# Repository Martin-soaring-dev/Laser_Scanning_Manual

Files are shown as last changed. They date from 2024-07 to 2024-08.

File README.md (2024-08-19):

# Extrusion 3D printer with integrated laser profile sensor - in NUS

[TOC]

## 一、简介（Introduction）

2D激光轮廓传感器(2D Laser profile sensor)集成到3D打印机中以实现3D扫描，如下所示。

该系统由传感器、运动控制平台(motion control platform)和气动挤压系统(pneumatic extrusion system)组成，通过以太网(Ethernet)或串口(Serial Port)与PC机连接。

打印Gcode由开源切片软件生成，并由开源用户界面(UI)软件读取和发送。

打印时，命令由PC通过串口发送到控制板，在控制板(control board)上解码并执行。

在matlab中编写了一套实现扫描功能的程序。

扫描时需要运动与传感器的协调，PC通过串口控制运动平台移动一步，再通过以太网与传感器通讯获取截面，如此循环直至扫描完成。

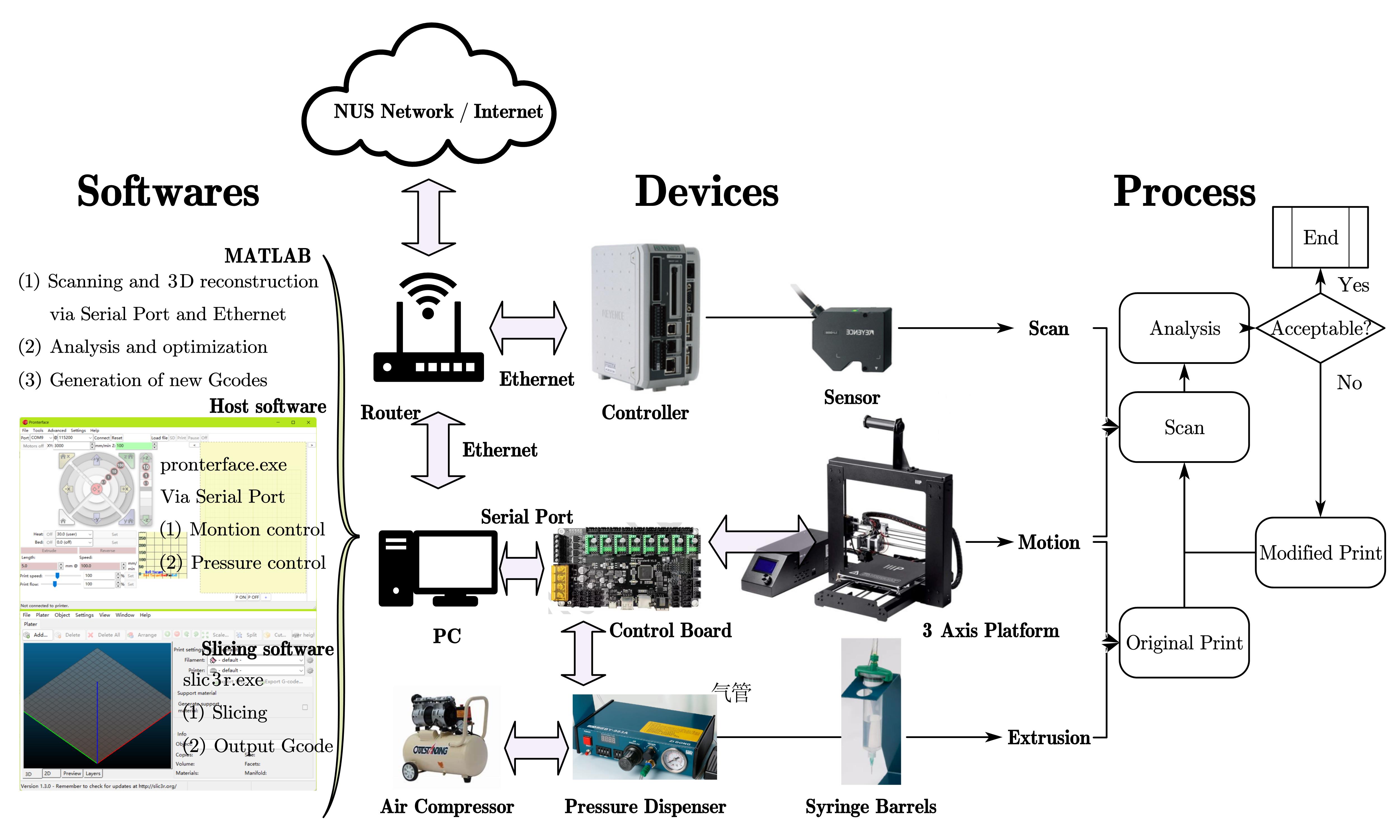
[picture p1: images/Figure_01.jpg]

图1 系统框图

### 如何从0开始搭建整个系统呢？

1. 购买/制造相应的组件，并按照设计进行装配
2. 确定各个端子的对应情况，并完成接线
3. 完成PC的环境准备、打印系统和扫描系统的配置
   1. 电脑环境的准备
   2. 打印和挤出系统的配置
   3. 扫描系统的配置

## 二、结构（Structure）

本节将介绍系统内部的主要结构。

### (1) 运动控制平台（Motion Control Platform）
运动控制平台是一个三轴钻床的基础上改装的。

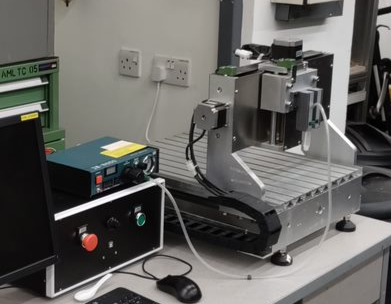
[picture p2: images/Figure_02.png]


图2 运动平台（原始） 

定制了如下组件：

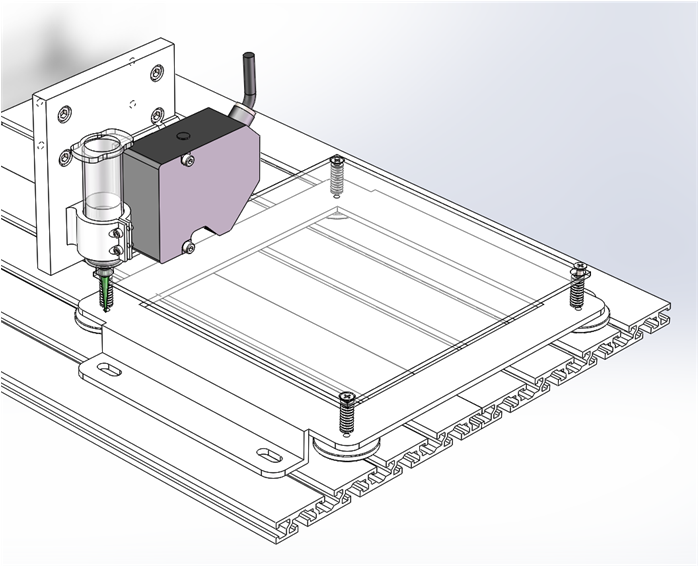
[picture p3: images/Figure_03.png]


图3 改造示意图 

#### 1）安装板
介绍：安装在Z轴滑板上的安装板，将注射器针筒和2D轮廓传感器安装在它上面。

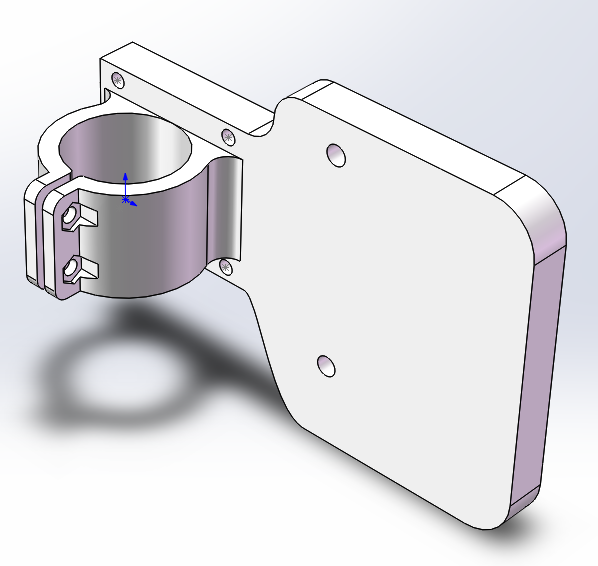
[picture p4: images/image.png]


制造：3D打印（FDM），工程塑料。

模型 3D Model：[click to get stl file](<3Dmodels/STL/安装板 - PlanB.STL>)

#### 2）底座组件

介绍：由基板、调节装置和底座构成。

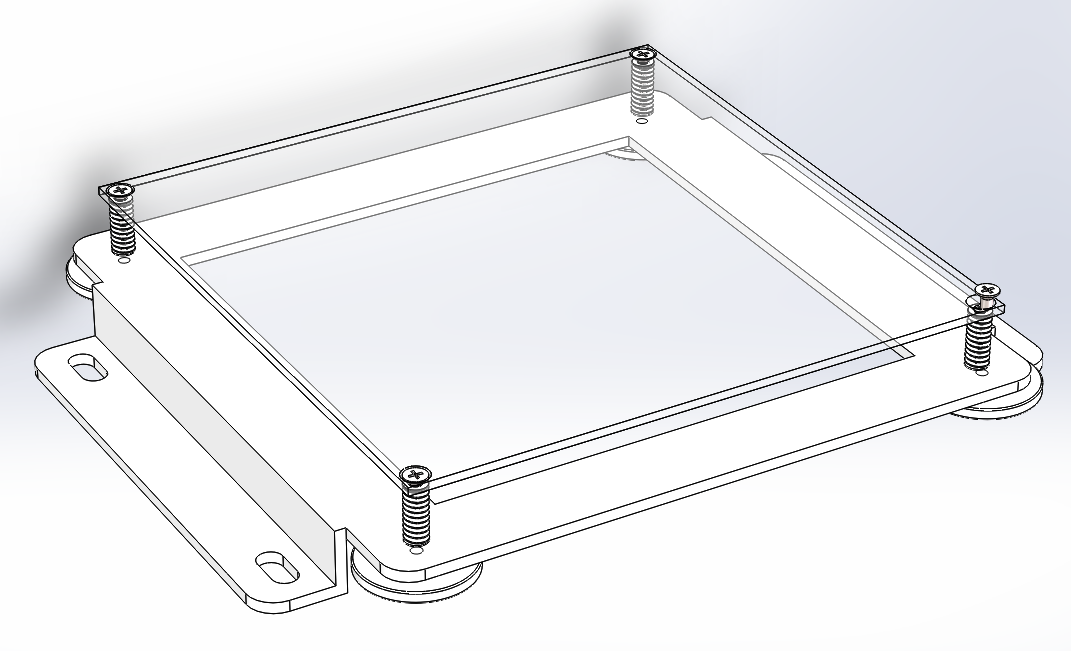
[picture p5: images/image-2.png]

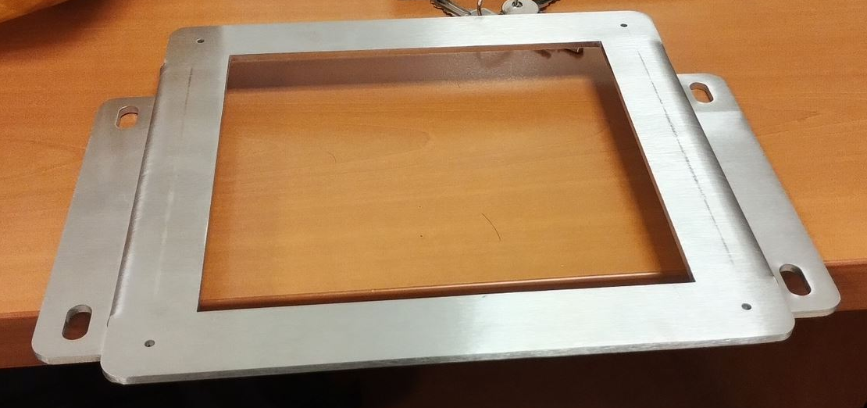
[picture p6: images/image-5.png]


制造：底座材料为不锈钢，通过激光切割和折弯制造。其余部件可直接采购。

模型 3D Model：[click to get stl file](<3Dmodels/STL/底座.STL>)

#### 3）装配体

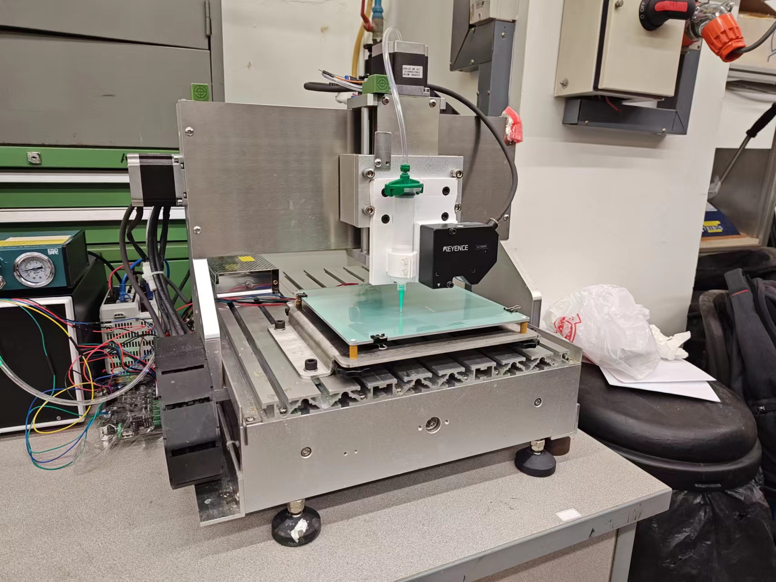
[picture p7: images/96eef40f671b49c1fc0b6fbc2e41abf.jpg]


图4 运动平台（改造后）

装配体 Assembly：[click to get stl file](<3Dmodels\STP\Assembly - Carriage-Z.STEP>)

### (2) 挤出系统（Extrusion System）
挤出系统由气压分配器和挤出装置构成。气泵可根据实验室条件选购。
#### 1）气压分配器（Pressure Dispenser）
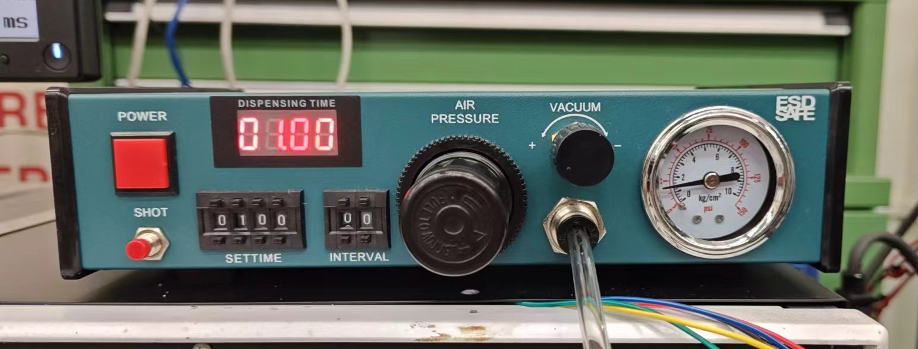
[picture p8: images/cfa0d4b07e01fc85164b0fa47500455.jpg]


图5 气压分配器

##### 技术指标：
1. 吐出方式：16种自由设定方式、带吐出时间显示*
2. 自动定时吐出：00.01S-99.99S
3. 吐出间隔时间：0.1-9.9S（自动定时功能）
4. 输入电压：220V±10% 50Hz/110V±10% 60Hz
5. 内部电压：12VDC/24VDC
6. 输入气压：10-100pSi
7. 输出气压：1-80 pSi
8.  外形尺寸：235×225×63mm
9.  重量：2.8kg
##### 使用安装说明:
位于背部的SETUP四位吐出时间编程器拨码开关，通过拨动其可作16种出方式选择模式组合设定如下：
<table>
<capital>模式组合</capital>
<tr>
<th rowspan=2 align="center">序号</th>
<th colspan=4 align="center"> 模式开关状态</th>
<th rowspan=2 align="center">吐出方式及工作对应功能</th>
</tr>
<tr>
<th align="center">S1</th>
<th align="center">S2</th>
<th align="center">S3</th>
<th align="center">S4</th>
</tr>
<tr>
<th align="center">1</th>
<th align="center">Off</th>
<th align="center">Off</th>
<th align="center">Off</th>
<th align="center">Off</th>
<th align="left">  点动模式，按下/踩下并保持以维持挤出</th>
</tr>
<tr>
<th align="center">2</th>
<th align="center">On</th>
<th align="center">Off</th>
<th align="center">On</th>
<th align="center">On</th>
<th align="left">  保持模式，按下/踩下1次开关，按照设定的时间持续挤出；再按下/踩下1次开关停止挤出。</th>
</tr>
<tr>
<th align="center">3</th>
<th align="center">Off</th>
<th align="center">On</th>
<th align="center">On</th>
<th align="center">On</th>
<th align="left">  点动计时模式，按下/踩下并保持以维持挤出设定的时间</th>
</tr>
<tr>
<th align="center">4</th>
<th align="center">On</th>
<th align="center">On</th>
<th align="center">On</th>
<th align="center">On</th>
<th align="left">  按照设定的时间自动定时连续挤出</th>
</tr>
<tr>
<th align="center">5</th>
<th align="center">On</th>
<th align="center">Off</th>
<th align="center">Off</th>
<th align="center">Off</th>
<th align="left">  按下/踩下1次开关，按设定时间挤出1次。</th>
</tr>
<tr>
<th align="center">6</th>
<th align="center">Off</th>
<th align="center">On</th>
<th align="center">Off</th>
<th align="center">Off</th>
<th align="left">  按下/踩下1次开关，按设定时间挤出2次。</th>
</tr>
<tr>
<th align="center">7</th>
<th align="center">On</th>
<th align="center">On</th>
<th align="center">Off</th>
<th align="center">Off</th>
<th align="left">  按下/踩下1次开关，按设定时间挤出3次。</th>
</tr>
<tr>
<th align="center">8</th>
<th align="center">Off</th>
<th align="center">Off</th>
<th align="center">On</th>
<th align="center">Off</th>
<th align="left">  按下/踩下1次开关，按设定时间挤出4次。</th>
</tr>
<tr>
<th align="center">9</th>
<th align="center">On</th>
<th align="center">Off</th>
<th align="center">On</th>
<th align="center">Off</th>
<th align="left">  按下/踩下1次开关，按设定时间挤出5次。</th>
</tr>
<tr>
<th align="center">10</th>
<th align="center">Off</th>
<th align="center">On</th>
<th align="center">On</th>
<th align="center">Off</th>
<th align="left">  按下/踩下1次开关，按设定时间挤出6次。</th>
</tr>
<tr>
<th align="center">11</th>
<th align="center">On</th>
<th align="center">On</th>
<th align="center">On</th>
<th align="center">Off</th>
<th align="left">  按下/踩下1次开关，按设定时间挤出7次。</th>
</tr>
<tr>
<th align="center">12</th>
<th align="center">Off</th>
<th align="center">Off</th>
<th align="center">Off</th>
<th align="center">On</th>
<th align="left">  按下/踩下1次开关，按设定时间挤出8次。</th>
</tr>
<tr>
<th align="center">13</th>
<th align="center">On</th>
<th align="center">Off</th>
<th align="center">Off</th>
<th align="center">On</th>
<th align="left">  按下/踩下1次开关，按设定时间挤出9次。</th>
</tr>
<tr>
<th align="center">14</th>
<th align="center">Off</th>
<th align="center">On</th>
<th align="center">Off</th>
<th align="center">On</th>
<th align="left">  按下/踩下1次开关，按设定时间挤出10次。</th>
</tr>
<tr>
<th align="center">15</th>
<th align="center">On</th>
<th align="center">On</th>
<th align="center">Off</th>
<th align="center">On</th>
<th align="left">  按下/踩下1次开关，按设定时间挤出11次。</th>
</tr>
<tr>
<th align="center">16</th>
<th align="center">Off</th>
<th align="center">Off</th>
<th align="center">On</th>
<th align="center">On</th>
<th align="left">  按下/踩下1次开关，按设定时间挤出12次。</th>
</tr>
</table>

实际使用的模式为序号1.

##### 操作：
1. 调压：通过调节黑色旋钮调节气压
2. 开关：可以按下左侧红色小按钮进行手动调节，也可以外接踏板手动调节（这个接口被改造用于程序控制）；控制方式在手册中有详细说明。
##### 参考资料
1. [手册](Docs/JND-983A点胶机详细功能设置.docx)

#### 2） 注射器针筒
##### 三维模型
1. [针筒](3Dmodels/SLDPRT/syringe.zip)
2. [喷嘴](3Dmodels/SLDPRT/tips.rar)
##### 手册
1. [喷嘴型号](Docs/技术表格.pdf)

### (3) 2D激光轮廓传感器（2D laser profile sensor）

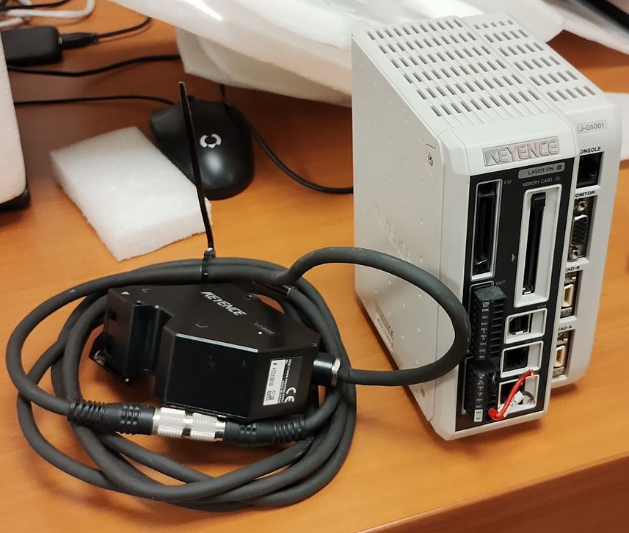
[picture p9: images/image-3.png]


图6 激光轮廓传感器

#### a. 概况：
使用的是基恩士2D激光轮廓传感器，驱动器型号为LJ-G5001，传感器型号为LJ-G030.

##### i. 驱动器：
驱动器基本安装尺寸如下所示：

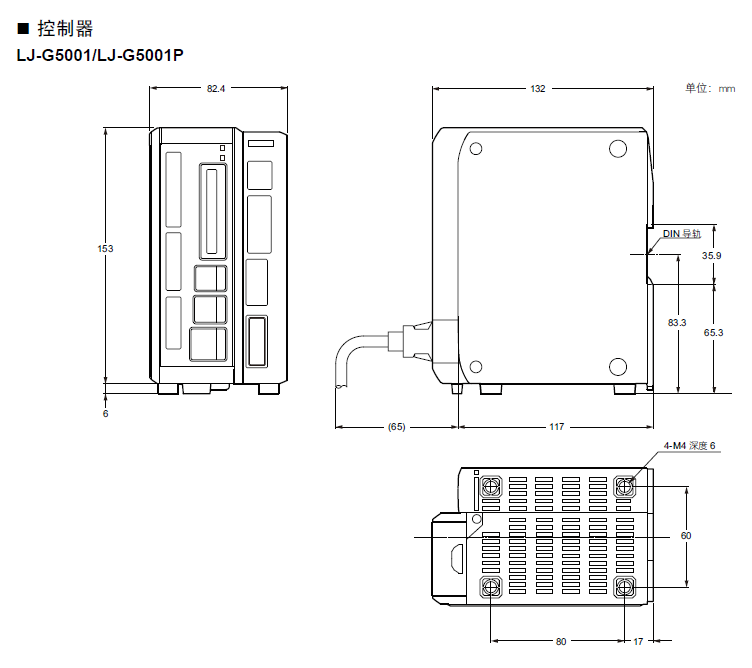
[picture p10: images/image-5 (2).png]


##### ii. 传感器：
1. 安装尺寸：

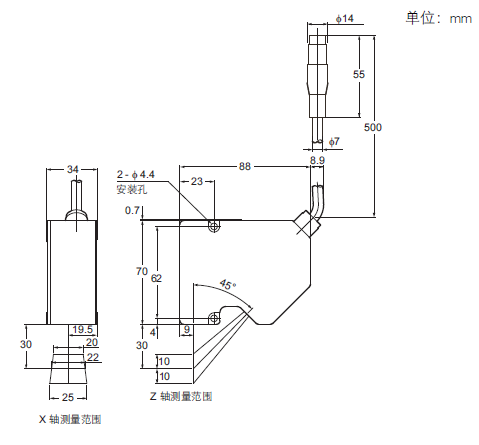
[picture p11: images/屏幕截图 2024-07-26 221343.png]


2. 测量原理及测量范围
激光轮廓传感器采用激光三角反射式原理：激光束被放大形成一条激光线投射到被测物体表面上，反射光透过高质量光学系统，被投射到成像矩阵上，经过计算得到传感器到被测表面的距离（Z 轴）和沿着激光线的位置信息（X 轴）。移动被测物体或轮廓仪探头，就可以得到一组三维测量值。

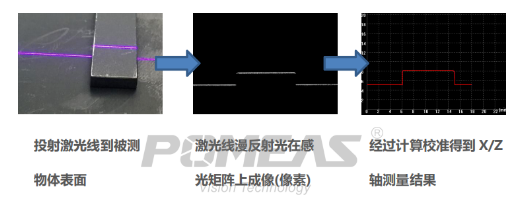
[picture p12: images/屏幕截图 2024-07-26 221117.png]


对于LJ-G030侧头，其有效测量区域为一个梯形，如下图所示：

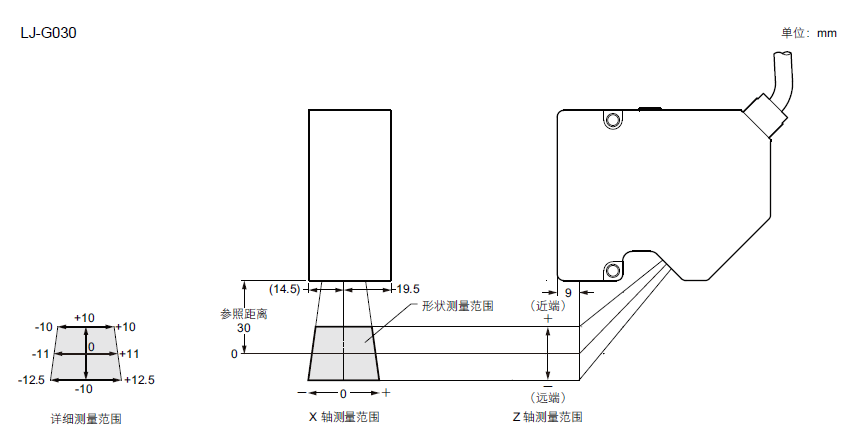
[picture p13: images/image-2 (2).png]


Z向测量范围：侧头下方30mm ± 10 mm；X向测量范围为 ±11 mm。

3. 测量精度：
Z向测量精度：1 μm. X向测量精度：5 μm。

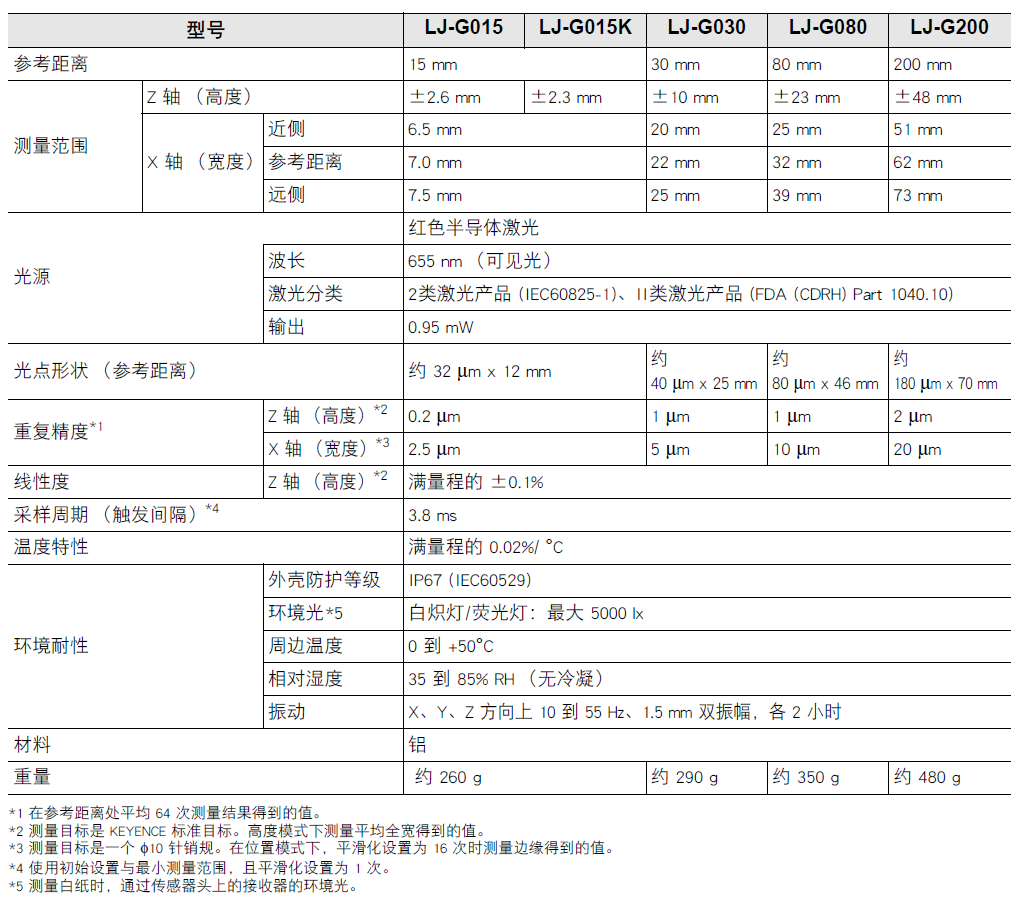
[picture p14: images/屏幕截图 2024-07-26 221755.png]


#### b. 通讯方式：

USB、串口、以太网。其中只有以太网通讯可以定制化传输轮廓数据。其他详情参见手册。
这里展示部分内容：

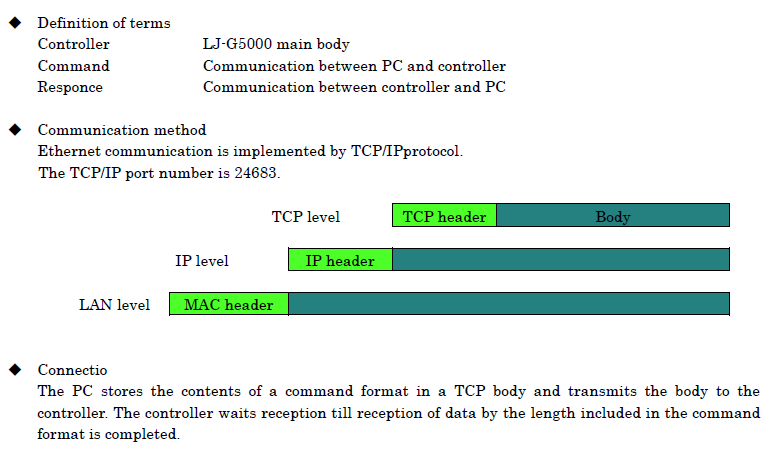
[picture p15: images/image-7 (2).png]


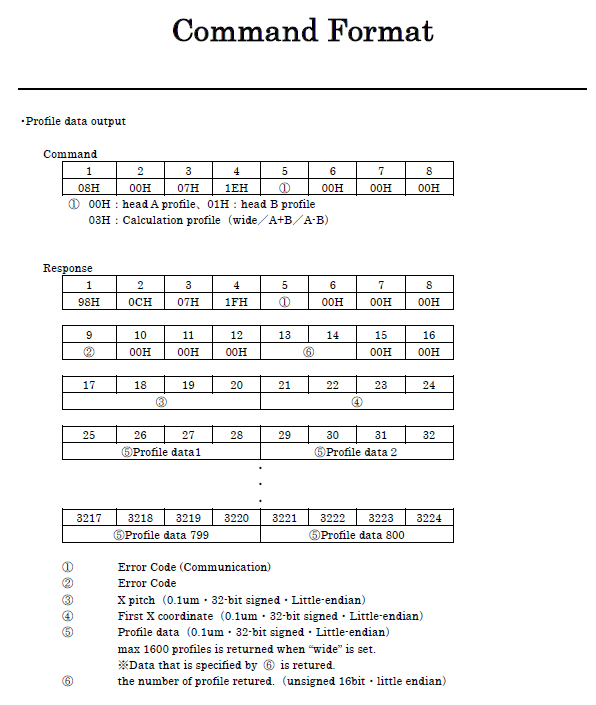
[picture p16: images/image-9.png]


#### 相关资料：
1. [用户手册](<Docs/01 AS_79826_LJ-G_UM_96M13960_CN_1059-7.pdf>)
2. [以太网通讯协议](<Docs/01 LJG5000_LAN.pdf>)
3. [LJ-G015 3D模型](Docs/LJ-G015(K)_2.x_t)
4. [LJ-G030 3D模型](Docs/LJ-G030_2.x_t)

## 三、硬件（Hardware）

这一节主要介绍接线和相关电路。

### (1) 控制板 Control borard
控制板采用了[创客基地(MakerBase)](https://makerbase.com.cn/)的[MKS-Monster8](https://github.com/makerbase-mks/MKS-Monster8)控制板。该控制板支持Marlin、Klipper等主流3D打印固件。

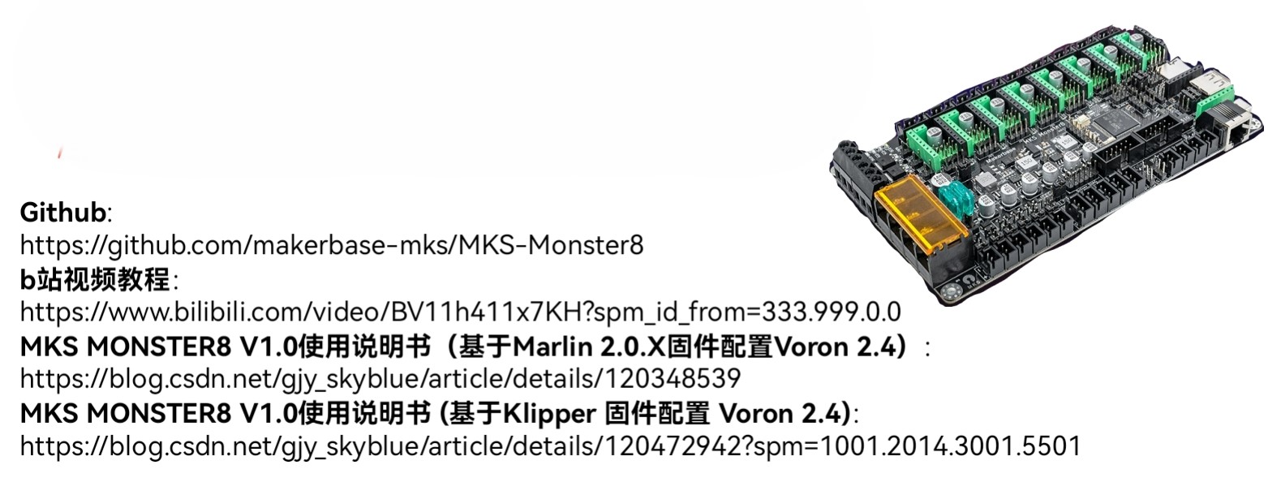
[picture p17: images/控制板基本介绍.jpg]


基本技术参数如下：
- MCU: STM32F407VET6, 168MHz, 512K flash, 192KB RAM
- 供电：DC12-24V input(2 MP1584EN Output DC12V(For FANs) and DC5V)
- 3 PWM FANs + 3 power output(all power can be select by jumper and select VIN, dc12V, dc5V)
- axis drivers and 9 motor interface(Driver0,1,2-1,2-2,3,4,5,6,7)
- EXP1,EXP2 support MKS MINI12864,MKS TS35,LCD12864,LCD2004
- USART(usart1:PA9,PA10) support MKS H43 or for other serial communication
- 6 endstop support power select(X-,X+,Y-,Y+,Z-,Z+) and 3D TOUCH(PA8) interface
- 4K eeprom on board(connect to I2C)
- Built-in CAN transceiver and interface(connect to CAN)
- Integrated SPI communication microsd card and reserved SPI signal interface
- Integrated UDISK
- Integrated virtural USB device
- Support TMC UART and SPI mode, SENSORLESS_HOMING function(Diag0-5,connect to X-,Y-,Z-,X+,Y+,Z+)
- Support driver power select(5V or 3.3V)
- Has TVS power spike protection
- Possess power reverse connection protection function
- Support DFU mode set by button(Boot0)

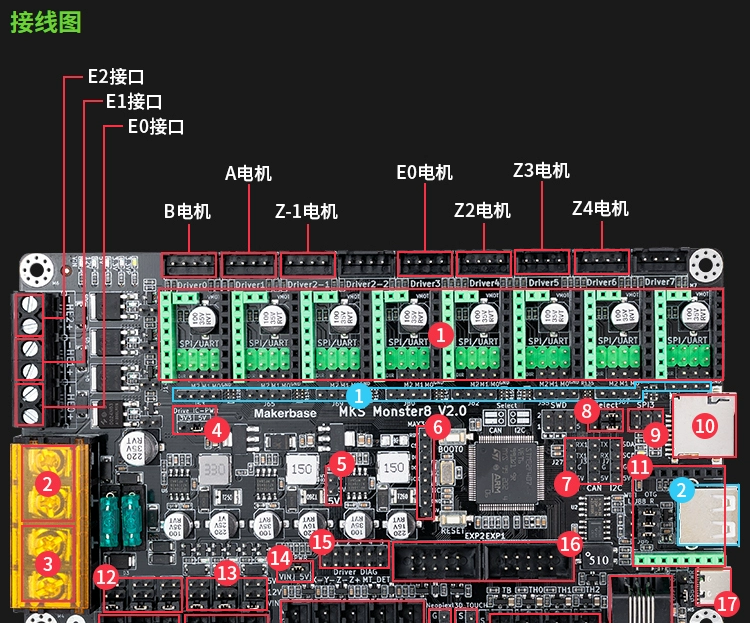
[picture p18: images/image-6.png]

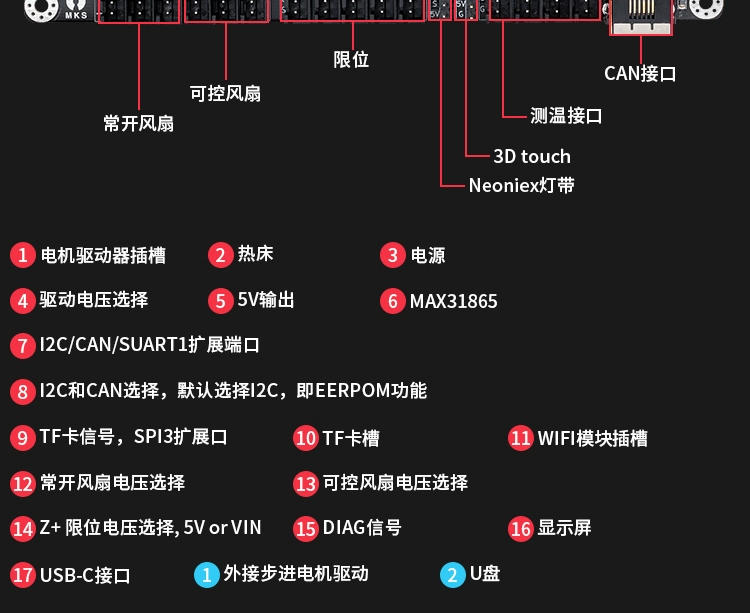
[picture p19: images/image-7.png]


但是，我们的平台需要使用的为X、Y、Z三轴的控制、无挤出加热需求、预留基板(substrate)的加热板(hot bed)，将风扇控制口留作气压开关(switch)控制，限位开关。综合上述考虑，大体的接线方案如下：

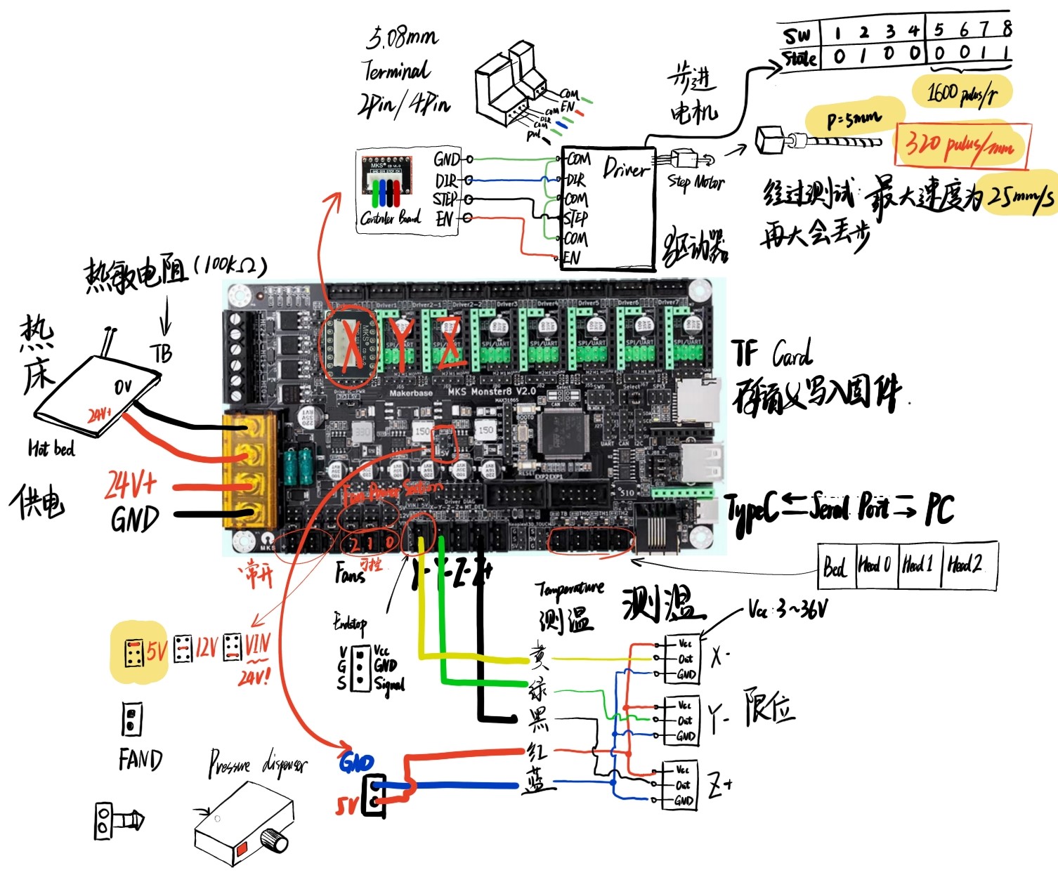
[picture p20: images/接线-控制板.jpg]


接线图

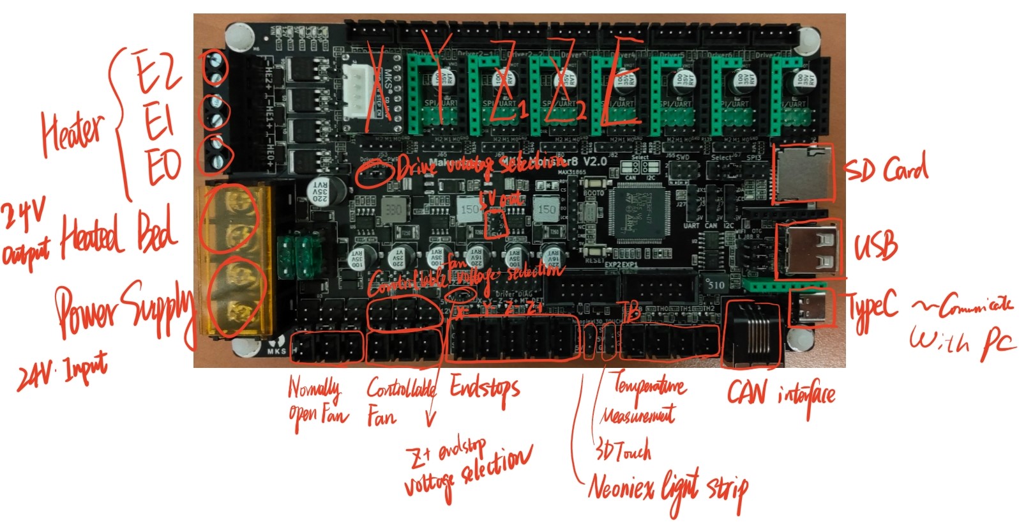
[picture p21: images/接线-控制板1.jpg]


接线图-补充

接下来我将结合这个整体接线图来说明各个部分是如何连接到控制板上的。

### (2) 电源 
电源用的就是很常见的220V交流输入，24V直流输出的电源。

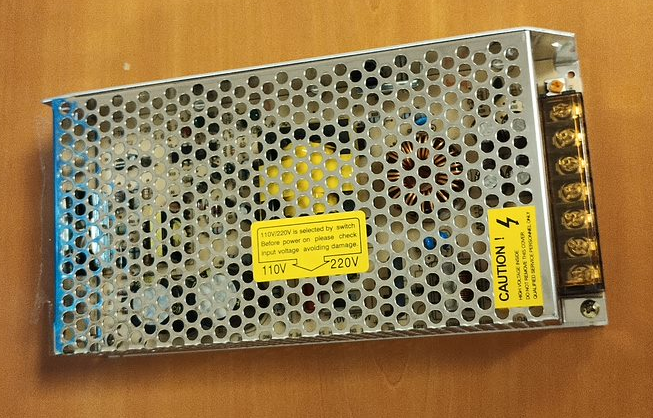
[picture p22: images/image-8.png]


图9 直流电源 Figure 9 DC power supply

### (3) 步进电机 Step Motors

所使用的点击为57步进电机。

步进电机首先与驱动器相连，驱动器需要接电源，并与控制板相连。

其控制方式为位置控制模式，即每发送一个脉冲，步进电机根据驱动器的设定转动特定的角度。对于57步进电机来说，步距角θ为0.8°（即1个脉冲对应电机轴转动0.8°），驱动可以设置系分数n，从而使得步距角变为θ/n，从而提高运动精度。只不过这种提升也是有限度的，通常认为细分数大于32时，对精度提升的效果会变得有限，细分数高于32时，主要的贡献在于提高运动的平稳性。

#### 驱动器

所使用的驱动器没有看到品牌和型号，但是将其设置面板抄了下来：

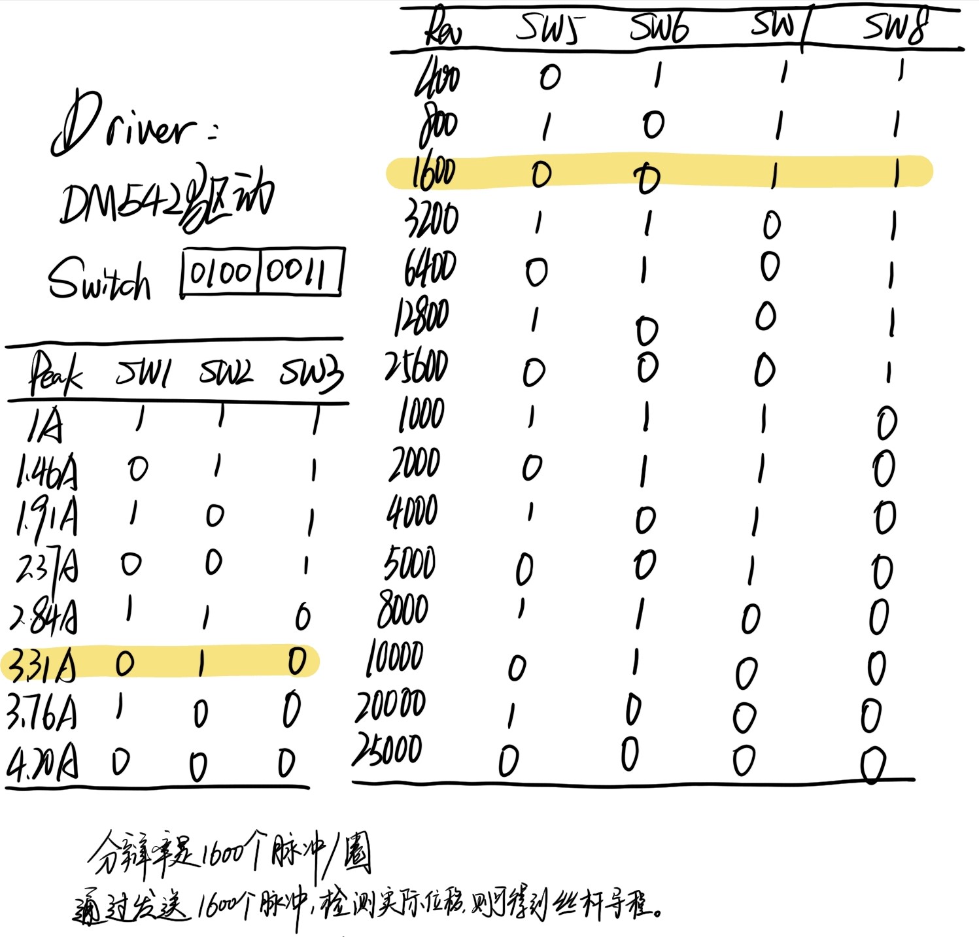
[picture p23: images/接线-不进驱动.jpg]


可以通过调整驱动器的拨码开关来调整电流峰值和细分数。突出显示的是原有配置，我沿用了该配置。

#### 接线

原先的接线方式如下：

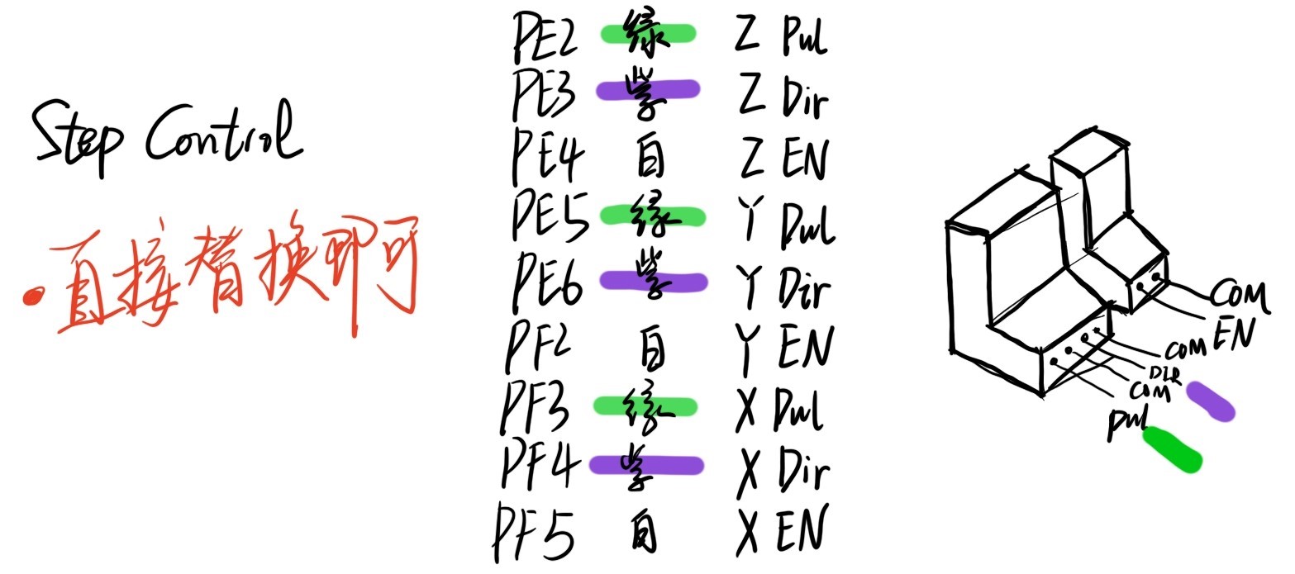
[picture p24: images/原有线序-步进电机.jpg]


参照原有接线方式进行接线。需要指出的是，使用了一个转接板直插到控制板上，然后再进行接线，公共端（COM）接地，其他的包括使能（Enable）、脉冲（Pulus）、方向（Direction）。并且线缆颜色与下图一一对应：

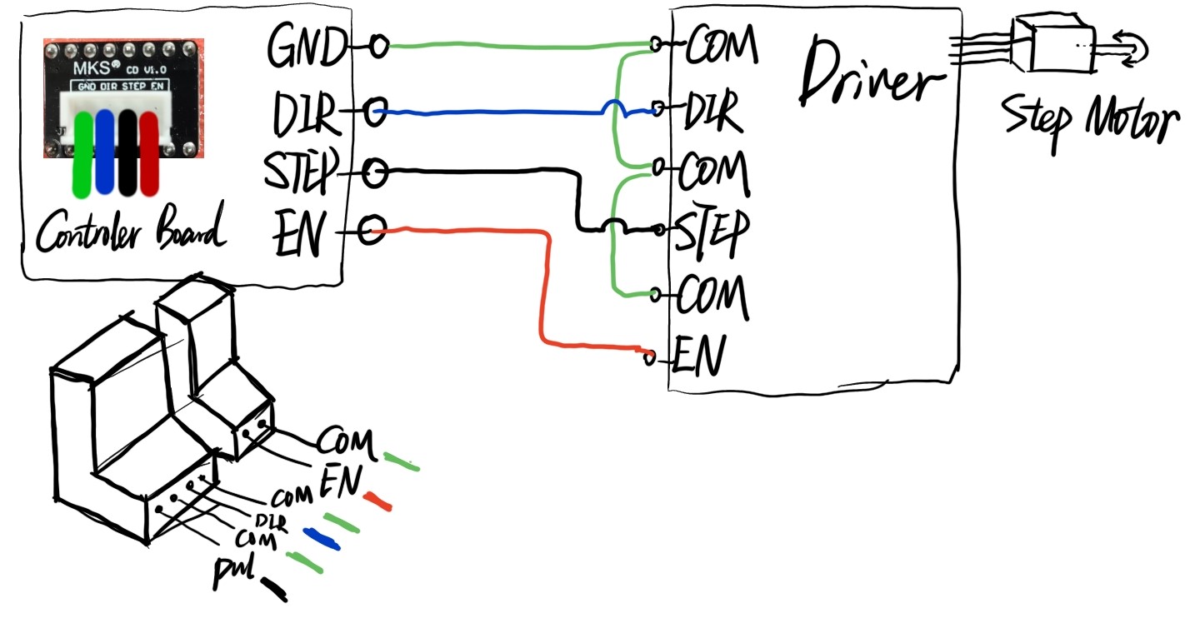
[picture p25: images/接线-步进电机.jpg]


### (4) 限位开关 Endstops

光电传感器，型号未知。根据原有接线方案调整：

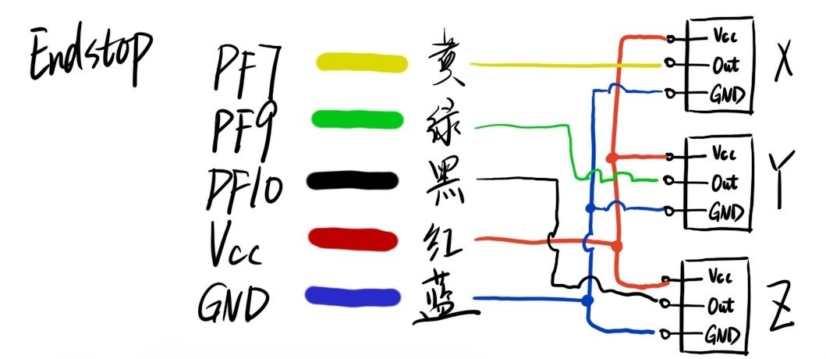
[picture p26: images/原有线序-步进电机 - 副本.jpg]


在实际调试过程中，发现原有的vcc 5V无法满足使用需要，有时候会出现电压不足的问题，且传感器上标识的工作电压为0~24V，因此选用24V电压作为供电。

可以在概览图中看到，在“接线图-补充”中，提到了Z+ endstop voltage selection, 在这里调整条线接法就能调整施加电压。

### (5) Hotbed
热床尺寸为210mm × 210mm

参考“接线图”进行接线即可，另外热床上有一个100k热敏电阻，需要借到“接线图-补充”中的TB处。

### (6) Pressure switch control

气压开关控制通过Controllable Fan端口控制，电压调整为24V，并接到继电器模块上，另外一端接到气压分配器(pressure dispenser)上，进而进行气压的开关控制(switch control)。

### (7) 传感器驱动器 Sensor Driver

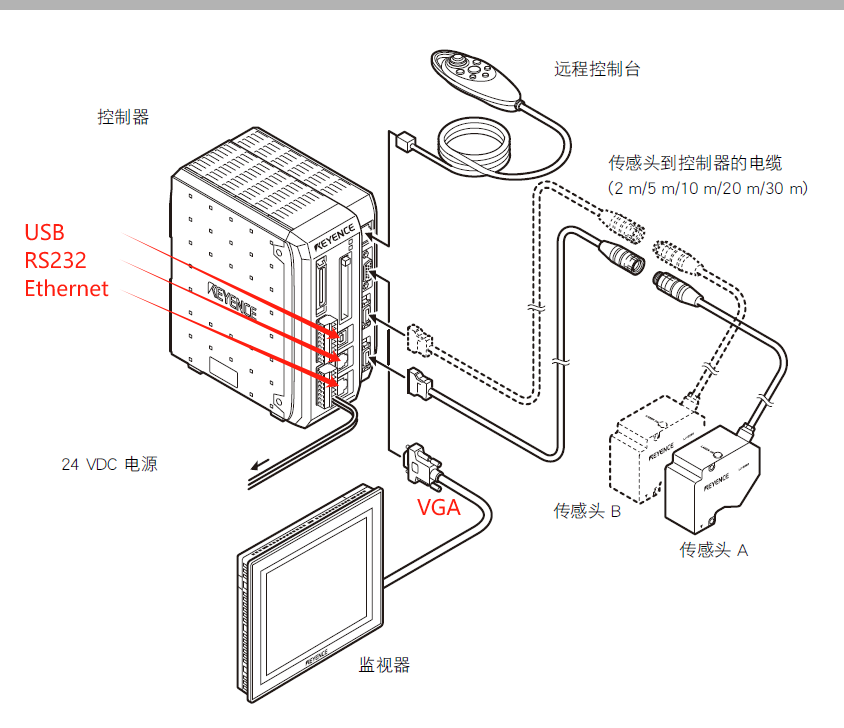
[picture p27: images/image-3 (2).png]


驱动器的接线方式参见上图：

①激光轮廓传感器需要接直流电源，电压为24V。

②可接显示器(VGA)观察轮廓信息。

③以太网口连接到路由器上从而与PC连接。也预留USB、RS232可以连接PC。

④传感器连接线。

## 四、Firmware - Marlin
[Marlin](https://marlinfw.org/)是最常用的开源3D打印固件，我们对其进行了相应修改，以满足设备使用：

1. 启用G05样条插补
2. 启用XYZ3个轴，并设定脉冲当量（每个轴移动1mm对应的脉冲数）
3. 关闭挤出机冷挤出限制（禁用温度传感器，设置最低挤出温度为0℃）
4. 按照实际行程范围调整配置打印范围。
5. 设置回零方向为X-，Y-，Z+

编程环境：VScode环境下使用PlatformIO插件。

Marlin官网：https://marlinfw.org/

原始Marlin资源：https://github.com/MarlinFirmware/Configurations/tree/release-2.1.2.4

定制Marlin资源：https://lecloud.lenovo.com/share/2JQMt9CWcRS9uVE4x （密码：pgjg）

## 五、软件 Software
这里分享使用的相关软件：

### （1）切片软件 Slicing software
#### 1）Slic3r
Slic3r是款开源切片软件，但是其已经停止开发了，所以存在一些bug。

官网：https://slic3r.org/

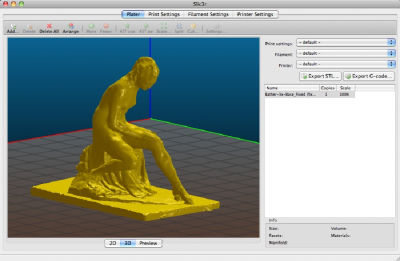
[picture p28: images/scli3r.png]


图13 Slic3r界面

#### 2）PrusaSlicer

是Slic3r的一个分支，目前仍然在开发，并且其社区相对活跃。之前使用Slic3r，但是因为BUG太多，现在已经转为使用PrusaSlicer。

官网：https://www.prusa3d.com/page/prusaslicer_424/

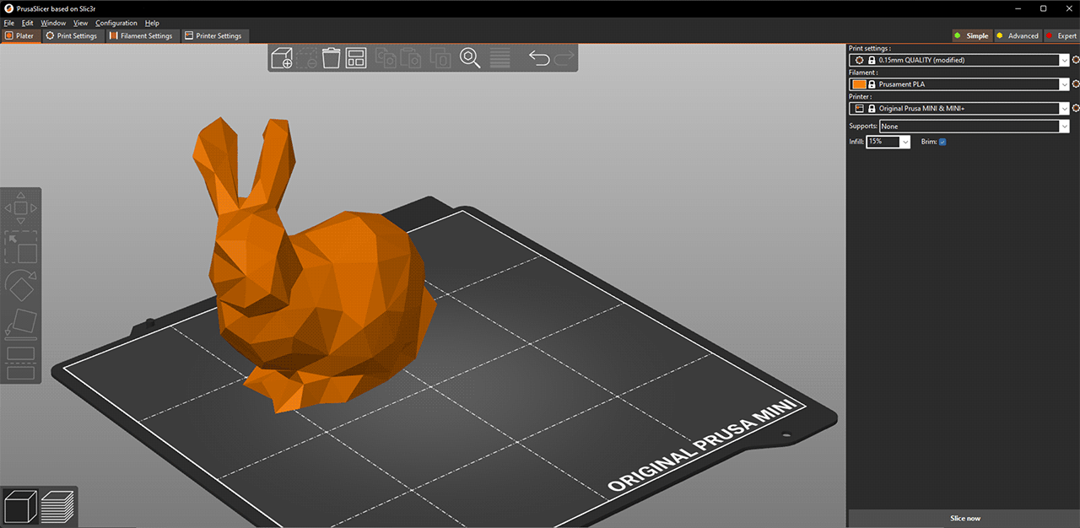
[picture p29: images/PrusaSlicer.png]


图14 PrusaSlicer界面

### （2）用户界面 user interface：pronterface   

官网：https://www.pronterface.com/

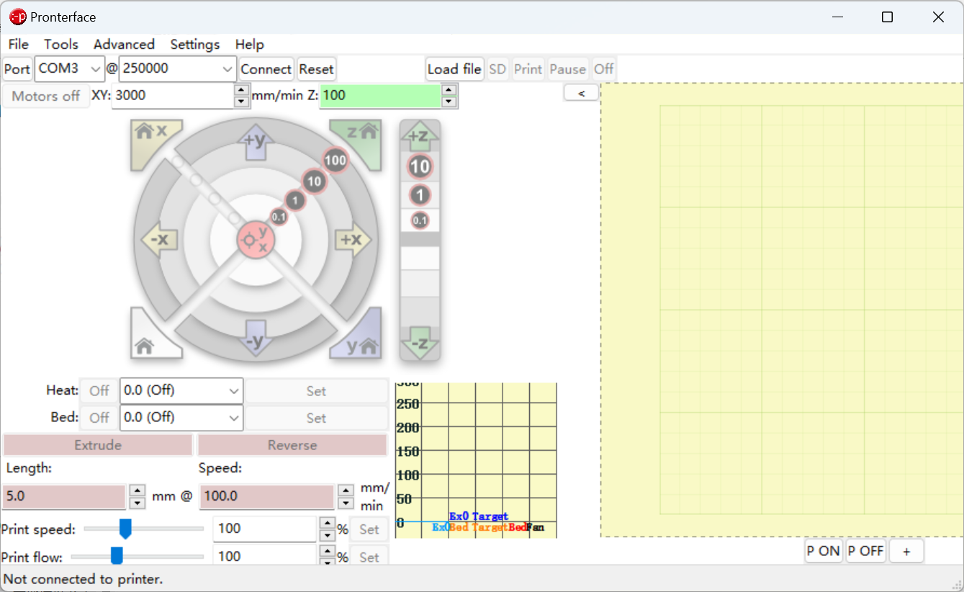
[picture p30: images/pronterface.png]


图15 界面

### （3）LJ-Navigator

基恩士激光轮廓传感器的官方软件，可以用来测试传感器和配置相关参数。

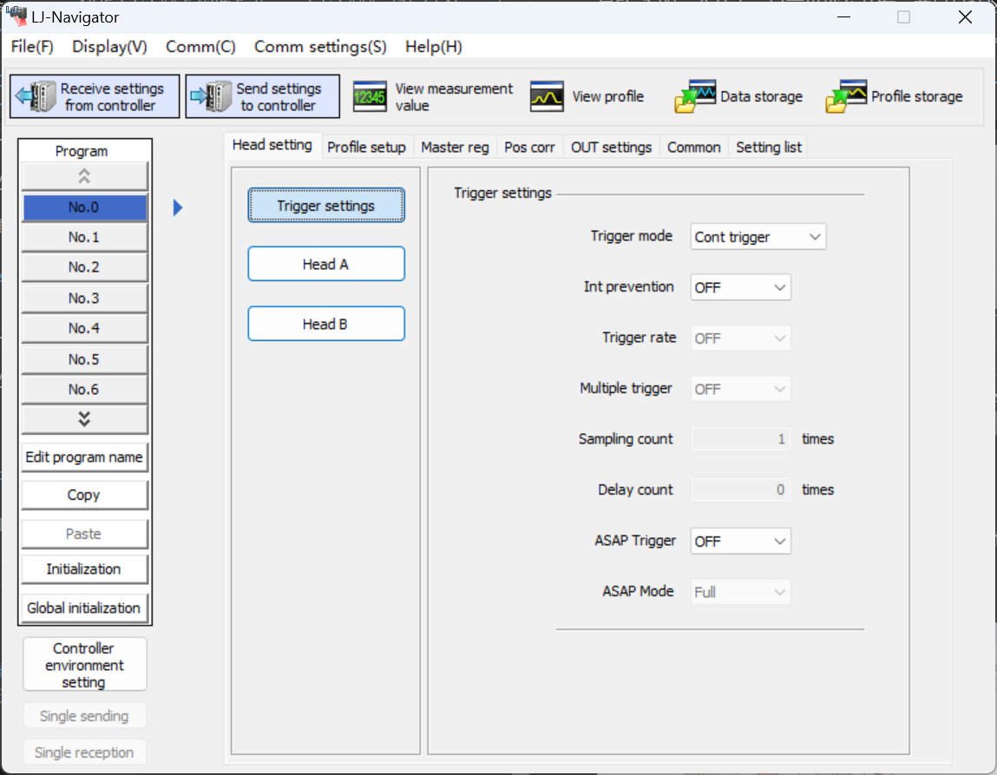
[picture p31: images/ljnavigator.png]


图16 界面

安装包：[LJ-Navigator](Docs/基恩士软件.rar)

### （4）CAXA 电子图版 2018 （中文版）
用于绘制打印、扫描轨迹

## 六、配置
### 1. 电脑环境的配置
系统：Windows 7/8/10/11都可以
软件：PrusaSlicer、pronterface、LJ-Navigator、CAXA、MATLAB。

### 2. 打印和挤出系统的配置
### （1）连接：

	将PC和控制板连接起来
### （2）确认端口号：

	此电脑[右击]→管理[打开“计算机管理”]→点击设备管理器→查看端口（找到连接控制板后新出现的端口，记住它）

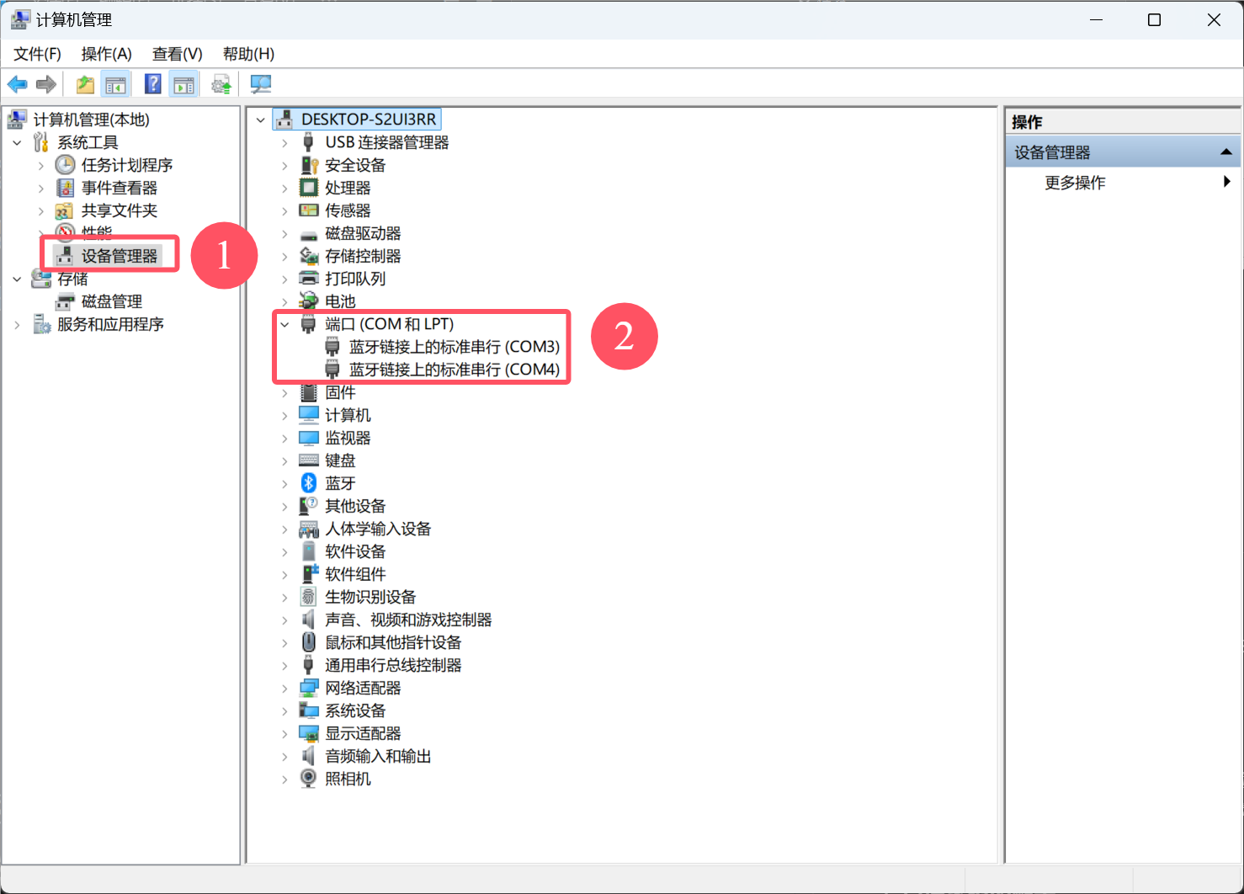
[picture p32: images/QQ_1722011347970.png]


### （3）通讯：

	打开"pronterface"然后选择刚才的端口号，配置波特率（默认250000）→连接
	然后就可以开始进行控制了，可以测试一下XYZ方向的移动，以及回零（测试限位开关），以及气压开关控制（手动输入M106/M107或如图配置两个按钮）。

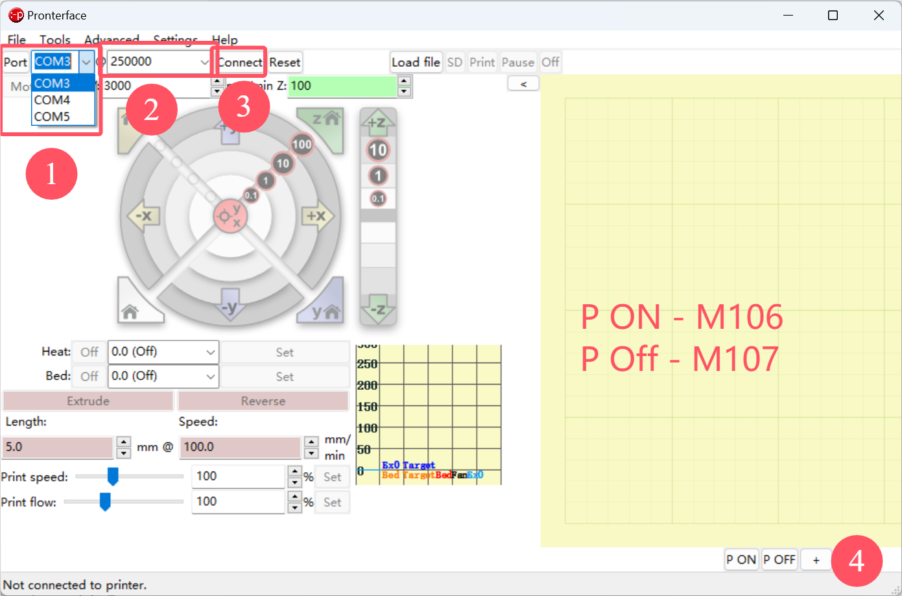
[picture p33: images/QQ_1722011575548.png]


### 3. 扫描系统的配置

### 3.1 建立通讯

（1）网络环境设置：[电脑]，关闭Wi-Fi，只连接以太网

（2）确定局域网IP：[电脑]，Win+R打开cmd（命令提示符），输入arp -a，找到接口，确定IP地址前几位为192.168.0.xxx/或者192.168.1.xxx

（3）设置驱动器IP：

	**方法1**：[驱动器]，在驱动器上用手柄控制进行设定：在传感器驱动器上：设定IP地址为192.168.0.xxx/或192.168.1.xxx（一般为101，如果101连不上，可以改为102，以此类推），重启设备，等待一会（更新配置），注意不要保持在环境设置的界面。

	**方法2**：[电脑]，使用USB连接后用LJ-Navigator进行设置。打开LJ-Navigator，选择合适的预设文件，然后选择好通讯方式（USB），接着接收设置。然后参考方法1进行IP地址的设置，完成后发送设置后重启即可。

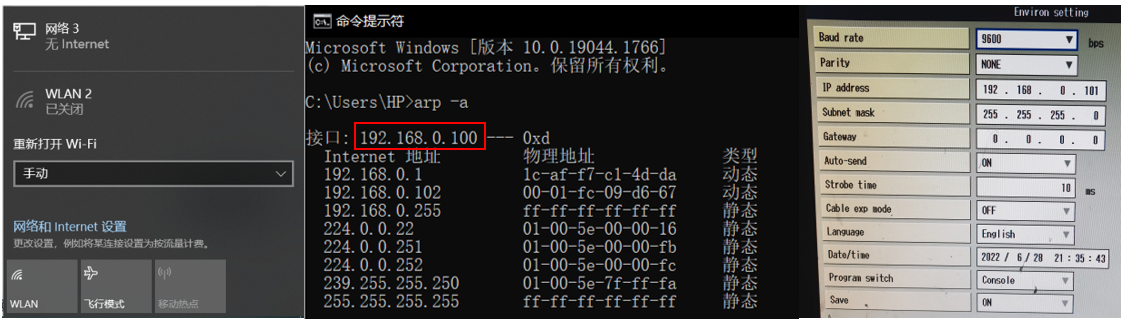
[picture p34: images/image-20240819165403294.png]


（4）软件设置：[电脑]，打开LJ-Navigator进行通讯设定。

- 打开LJ-Navigator后，选择使用默认设置，然后选择对应的激光轮廓传感器（如G015）：
- 通讯设定→PC通讯设定：选择通过以太网通讯，然后选择链接控制器，再点击检查控制器，稍等，然后点击下拉菜单，从而刷新局域网内的设备，若出现了刚才设定的IP则说明设定成功（传感器已经成功连入局域网）
- 点击Receive settings from controller，读取驱动器设定，从而测试连接。

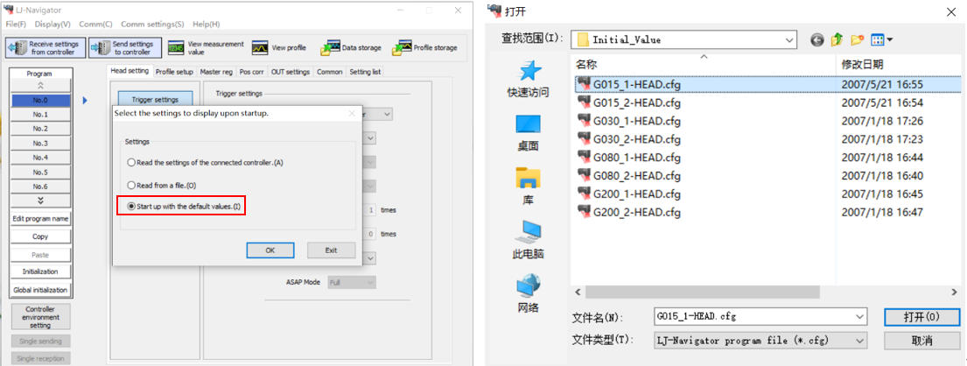
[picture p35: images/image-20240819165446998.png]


### 3.2 截面获取

#### 方法1：LJ-Navigator软件

1. 点击View profile，点击开始预览，从而获取显示扫描图像
2. 点击CSV output，输出800个z坐标信息（单位为mm，但会有错误点，错误点用-999.999表示，需剔除错误点）

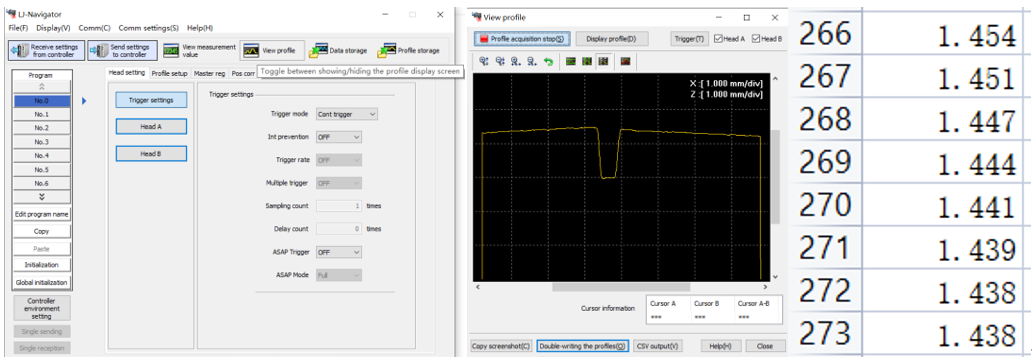
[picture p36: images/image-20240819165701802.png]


#### 方法2：MATLAB代码处理数据信息（相关代码在下一节介绍）

1. 在cmd中输入arp -a, 确定已经找到设定的IP（如果找不到的话：打开LJ-Navigator软件，测试能够正常通讯和查看截面，然后关闭软件）

2. 关闭所有程序和窗口

3. 在MATLAB中使用编写的函数通讯，处理数据，绘制截面。其中函数的语法为：

   `[coordinate,profile]=LJ_G5000_v1_2(ip,a)`

   其中：

   profile 是轮廓上各个点的高度数据，该数据为16位带符号的二进制数，最高位用于表示符号，后面15位用于表示数值，因此最大为
   $$
   2^{15}=32768
   $$
   ip地址是传感器的ip地址，例如’196.168.1.101’

   指令号是要对驱动器进行的操作，包括返回轮廓数据、测量值等。目前仅支持返回单测头轮廓数据，格式为Pk，其中k为测头序号。目前仅能使用’P1’指令。

   | 变量       | 含义          | 备注                                       |
   | ---------- | ------------- | ------------------------------------------ |
   | a          | 指令          |                                            |
   | 'Pk'       | 轮廓输出      | LJ_G5000_v1_2('192.168.1.101','P1')        |
   | ~~'Ma'~~   | 测量输出      | LJ_G5000_v1_2('192.168.1.101','M12345678') |
   | ~~'Q1'~~   | 通讯模式      | LJ_G5000_v1_2('192.168.1.101','Q1')        |
   | ~~'R0'~~   | 测量模式      | LJ_G5000_v1_2('192.168.1.101','R0')        |
   | coordinate | 轮廓横坐标(X) | 单位um                                     |
   | profile    | 轮廓纵坐标(Z) | 单位um                                     |

示例：

```matlab
[coordinate,profile] = LJ_G5000_v1_2('192.168.1.101','P1'); % 获取截面数据
plot(coordinate,profile) % 绘制截面形状
```

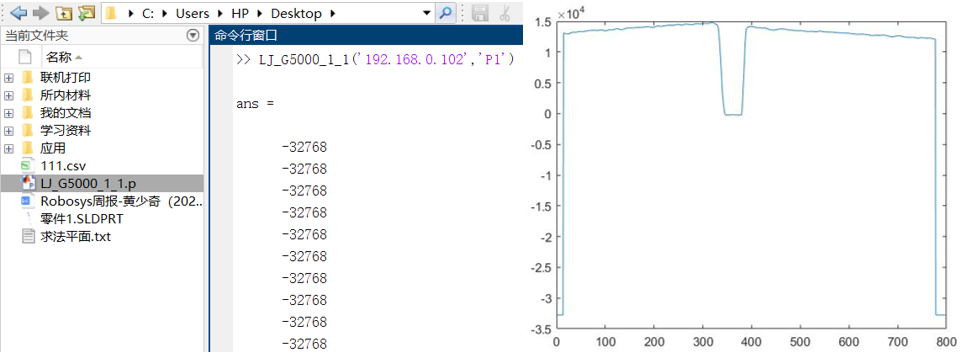
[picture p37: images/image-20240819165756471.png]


### 3.3 使用技巧

**（1）在建立链接时找不到激光位移传感器的IP地址**

	①在激光轮廓传感器中设置IP地址，注意，需要避开当前已占用的IP地址；设置完成后重启控制器，以更新配置；如果还未找到IP地址，则进行下一步；

	②打开LJ-Navigator，配置通讯设定并读取控制器设置，完成后在命令行中应该能够通过arp -a 刷新出控制器的IP地址。需要注意的是，使用LJ-Navigator时会占用TCPIP端口，如果需要在MATLAB中使用，则需要先退出该软件。

## 七、程序和代码

### 1. 截面获取

Matlab App Installation Package: [LJ_G5000_v1_2.mlappinstall](<Docs/LJ_G5000_v1_2.mlappinstall>) 

**（1）安装**：双击安装包即可，安装后可以在附加管理器中找到文件目录：

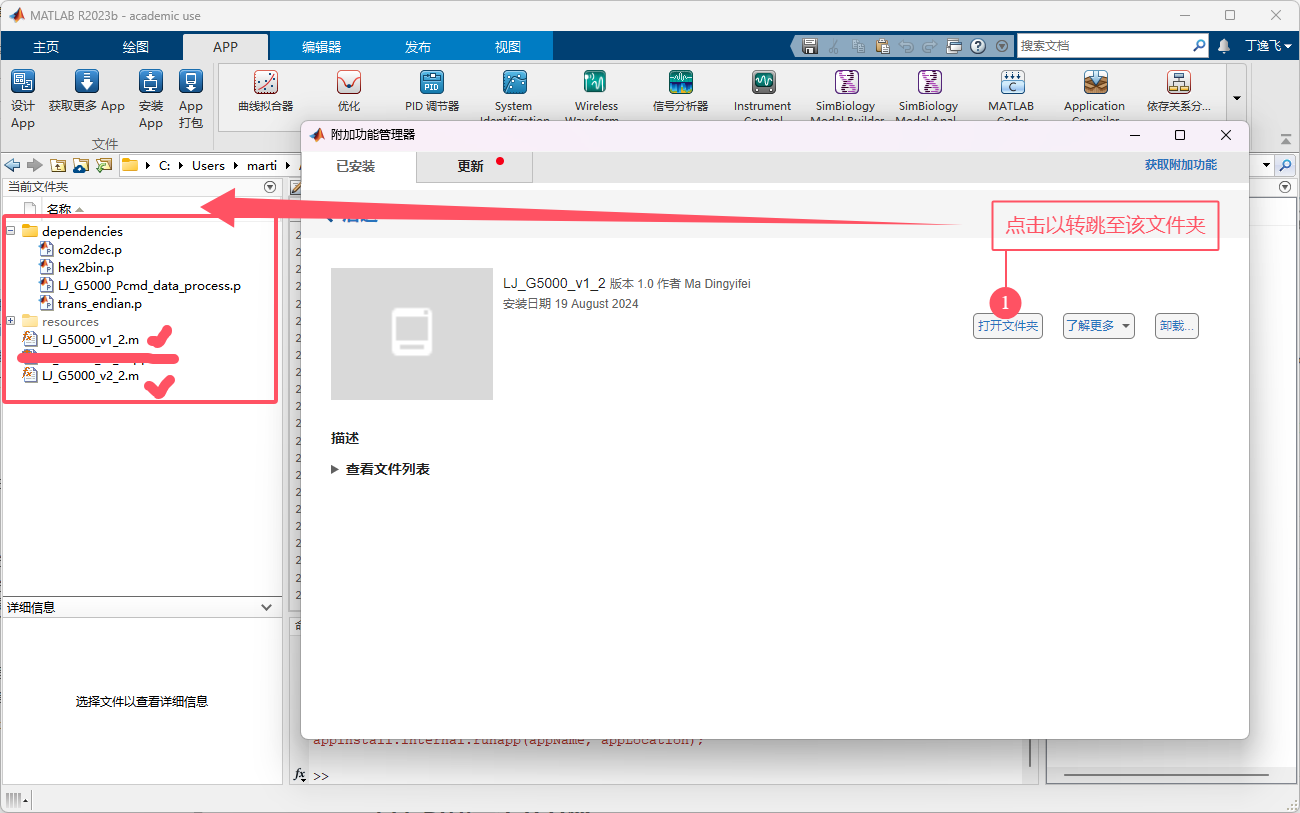
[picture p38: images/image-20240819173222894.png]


**（2）使用**：

	LJ_G5000_V1_2在上一节已经说过用法，在这不赘述。

	LJ_G5000_V2_2：在使用这个函数前，需要先自行建立全局(global)tcpip对象t，才能正常使用，调用时不需要再输入IP，直接输入指令即可。

**（3）说明**：

	两个函数都是基于LJG5000以太网通讯协议（ [01 LJG5000_LAN.pdf](Docs\01 LJG5000_LAN.pdf) ）文件编写的，LJ_G5000_V1_2的处理基本流程包括：建立TCPIP对象→建立通讯→**发送指令→接收数据→处理数据**→断开通讯→清除TCPIP对象，LJ_G5000_V2_2的目的是为了避免多次调用时，频繁建立和断开通讯，造成时间上的浪费，因此只保留了上述加粗部分的环节。

	特别的，如果使用的打印机可以通过串口Serial Port进行通讯，并进行运动控制。就可以以此控制打印机运动→获取截面的循环，从而获得三维轮廓。

## 八、Example (How to use)
### （1）打印一个立方体
### （2）获得一个截面轮廓
### （3）按照指定轨迹获取轮廓
### （4）设计打印轨迹并在打印后扫描，然后输出点云文件

# 参考文献

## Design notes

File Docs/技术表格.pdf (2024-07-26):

### Tapered Tips

Standard | Opaque Rigid | Gauge | Color | ID

Qty/

Box

7018052 | 7018049 | 14
Olive

1.60 mm

0.063"

50

7018100 | 7018097 | 16
Grey

1.19 mm

0.047"

50

7018158 | 7018147 | 18
Green

0.84 mm

0.033"

50

7005009 | 7005006 | 20
Pink

0.58 mm

0.023"

50

7018298 | 7005007 | 22
Blue

0.41 mm

0.016"

50

7018391 | 7018370 | 25
Red

0.25 mm

0.010"

50

7018417 | n/a | 27
Clear

0.20 mm

0.008"

50

7363483 | n/a | 27 | Black
| | | (ESD-safe)

0.20 mm

0.008"

50

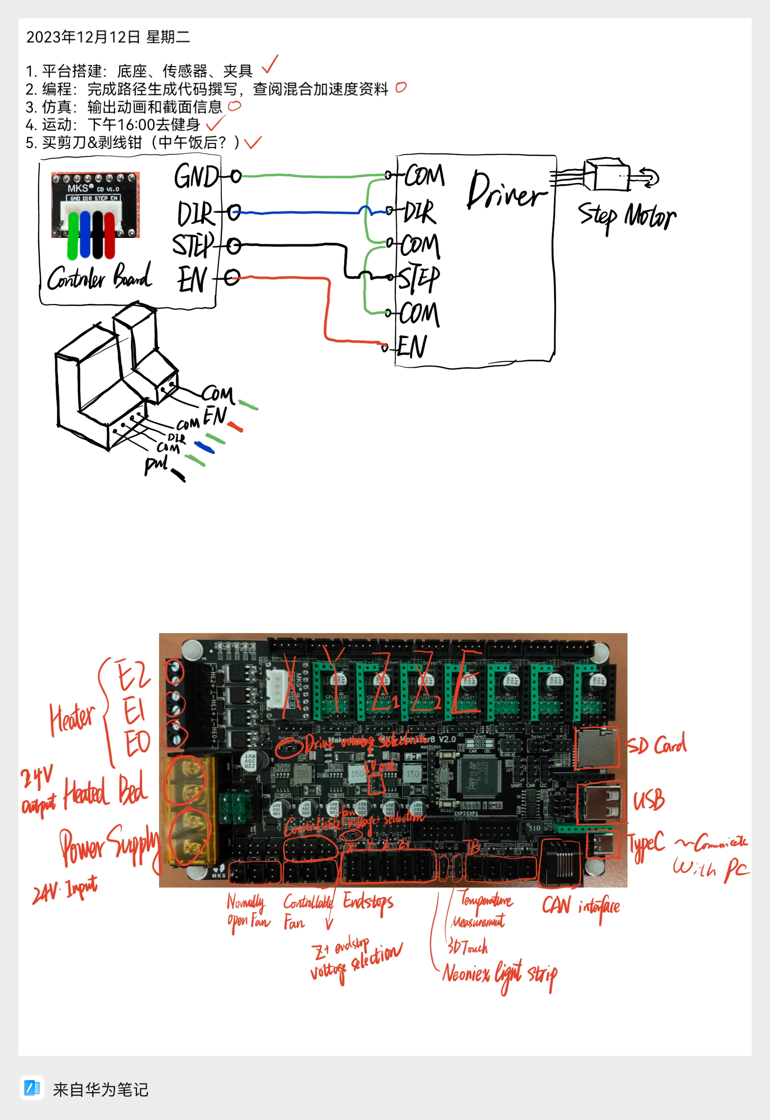
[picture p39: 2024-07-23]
images/2023年12月_202407231441_41358 10.jpg

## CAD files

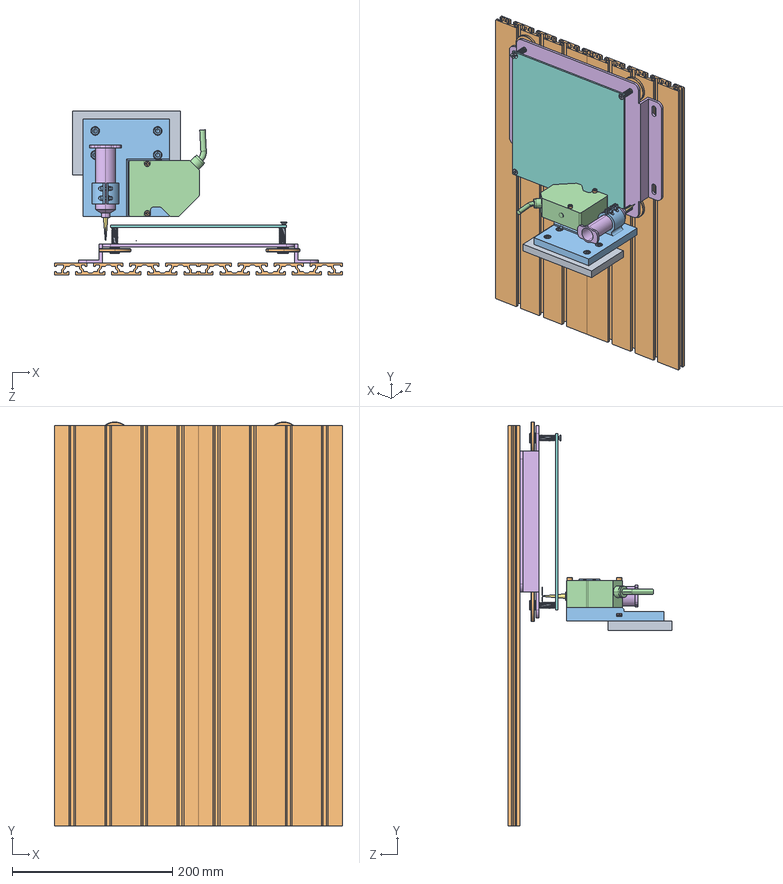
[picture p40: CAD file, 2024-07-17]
3Dmodels/STP/Assembly - Carriage-Z.STEP
360.0 x 504.5 x 205.0 mm
Carriage-Z
15180G x 2
假蚾啣 - PlanB
LJ-G030_2_______
注射器模型
注射器喷嘴模型
注射器硅胶模型
注射器活塞模型
hexagon socket head cap screws gb_GB_FASTENER_SCREWS_HSHCS M4X45-N x 2
hexagon socket head cap screws gb_GB_FASTENER_SCREWS_HSHCS M3X10-N x 2
hex thin nuts-grades b--unchamfered gb_GB_HEXAGON_TYPE5 M3-C x 2
hex thin nuts-grades ab-chamfered gb_GB_FASTENER_NUT_STNAB M4-N x 2
菁釱
粟銅 x 4
热床
cross recessed countersunk head screws gb1_GB_CROSS_SCREWS_TYPE4 M4X35-32.3 H type-N x 4
热床螺母 x 4
hexagon socket head cap screws gb_GB_FASTENER_SCREWS_HSHCS M6X16-C x 4

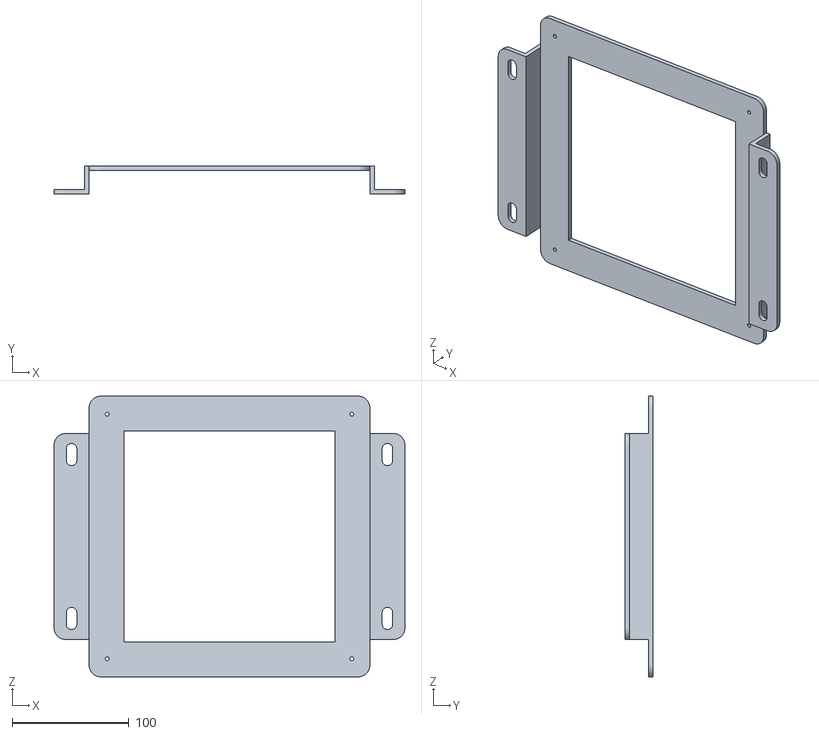
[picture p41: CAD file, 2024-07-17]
3Dmodels/STL/底座.STL
300.0 x 24.0 x 240.0

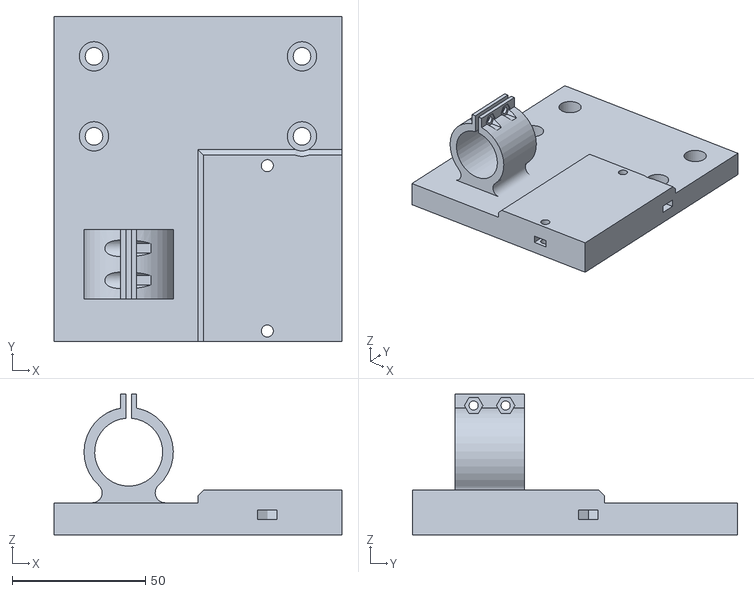
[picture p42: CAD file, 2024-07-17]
3Dmodels/STL/安装板 - PlanB.STL
108.0 x 122.0 x 52.7
